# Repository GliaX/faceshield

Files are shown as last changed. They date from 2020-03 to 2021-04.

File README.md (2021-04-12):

# Face Shield
The goal of this project is to create a low cost, high quality, reusable face
shield that can be quickly deployed.

This face shield is currently in use in London, Canada, the West Bank and Gaza Strip.

This face shield's 3D printed design was made by Jake Bender. Contributors include Mike Doell (@mike_doell)
and Mosaic Manufacturing. The injection-molded design was made by Abd Aliwa and Steve Plimmer and can be found at [this branch of the repository](https://github.com/GliaX/faceshield/tree/injection-mold).

To purchase, go to https://store.glia.org

# Bill of Materials
## Molded parts
* 1 head piece (headpiece.stl)

## Other hardware
* 60cm x 1cm Elastic strap
* Large: 28cm x 25cm with a thickness of 0.254mm clear plastic sheet such as Mylar (facesheet-large.svg)
* Small (default): 28cm x 23cm with a thickness of 0.254mm clear plastic sheet such as Mylar (facesheet-small.svg)

# Print instructions
* Use PETG or ABS
* Layer height: 0.3mm
* Use PrusaSlicer 2.2 or above to import 3MF file
* Modify filament and printer settings as needed
* **DO NOT MODIFY PRINT SETTINGS**
* Export and print

# Mylar sheet Instructions
* Cut the mylar sheet with a laser cutter or die cutting machine if available
* If a cutter is not available, you may manually cut the sheets to
28cm x 25cm. Consider rounding corners as per template

# Decontamination
* Disassemble head piece from strap and mylar sheet
* Soak entire shield and strap for 1 minute in warm bleach solution in well-ventilated area
* Rinse with water
* Hang to dry

# Assembly instructions
* See [Assembly Instructions illustration](instructions.jpg) for a visual guide
* Loop strap through strap holes on printed head piece
* Insert clear plastic sheet into printed head piece
* Fit can be adjusted by pulling on the loose ends of the elastic strap

# Licensing notes
As per our understanding, hardware is not covered by copyright. However, we
present our work under the TAPR OHL or GPLv3 licenses insofar as it applies.

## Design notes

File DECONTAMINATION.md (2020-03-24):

# Decontamination
* Make 5,000ppm bleach solution: 85mL of 6.25% hypochlorite household bleach in 1L warm water.
* Disassemble head piece from strap and mylar sheet
* Soak entire shield and strap for 1 minute in warm bleach solution in well-ventilated area
* Rinse with water
* Hang to dry

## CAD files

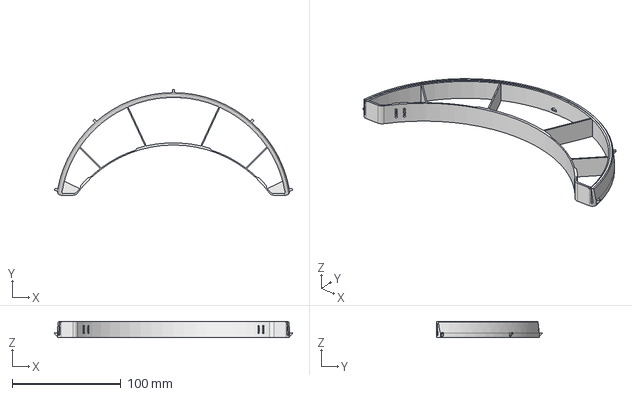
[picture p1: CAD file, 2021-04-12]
source/cad/headpiece.FCStd
218.4 x 96.8 x 15.0 mm

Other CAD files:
source/stl/headpiece.stl

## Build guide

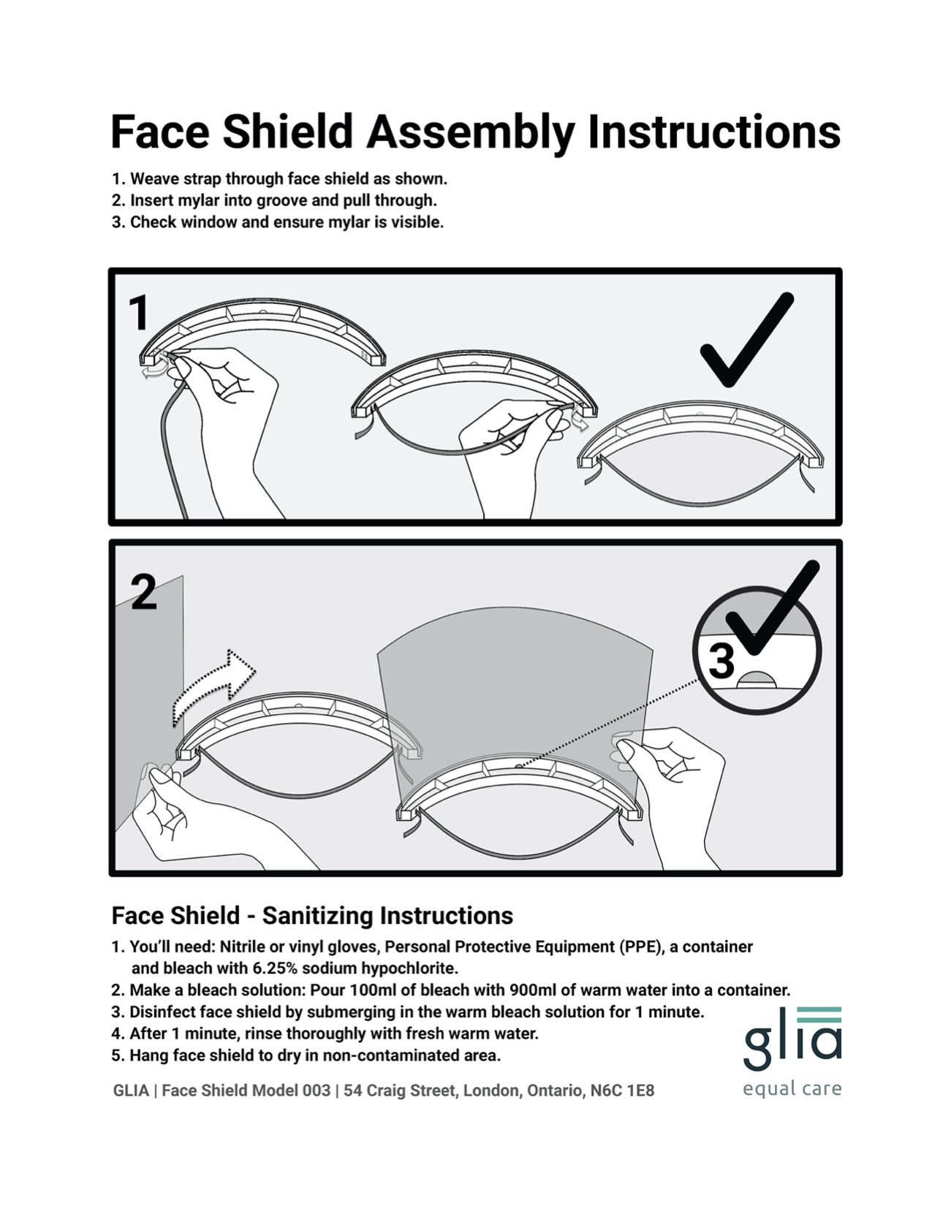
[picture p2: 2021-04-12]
instructions.jpg

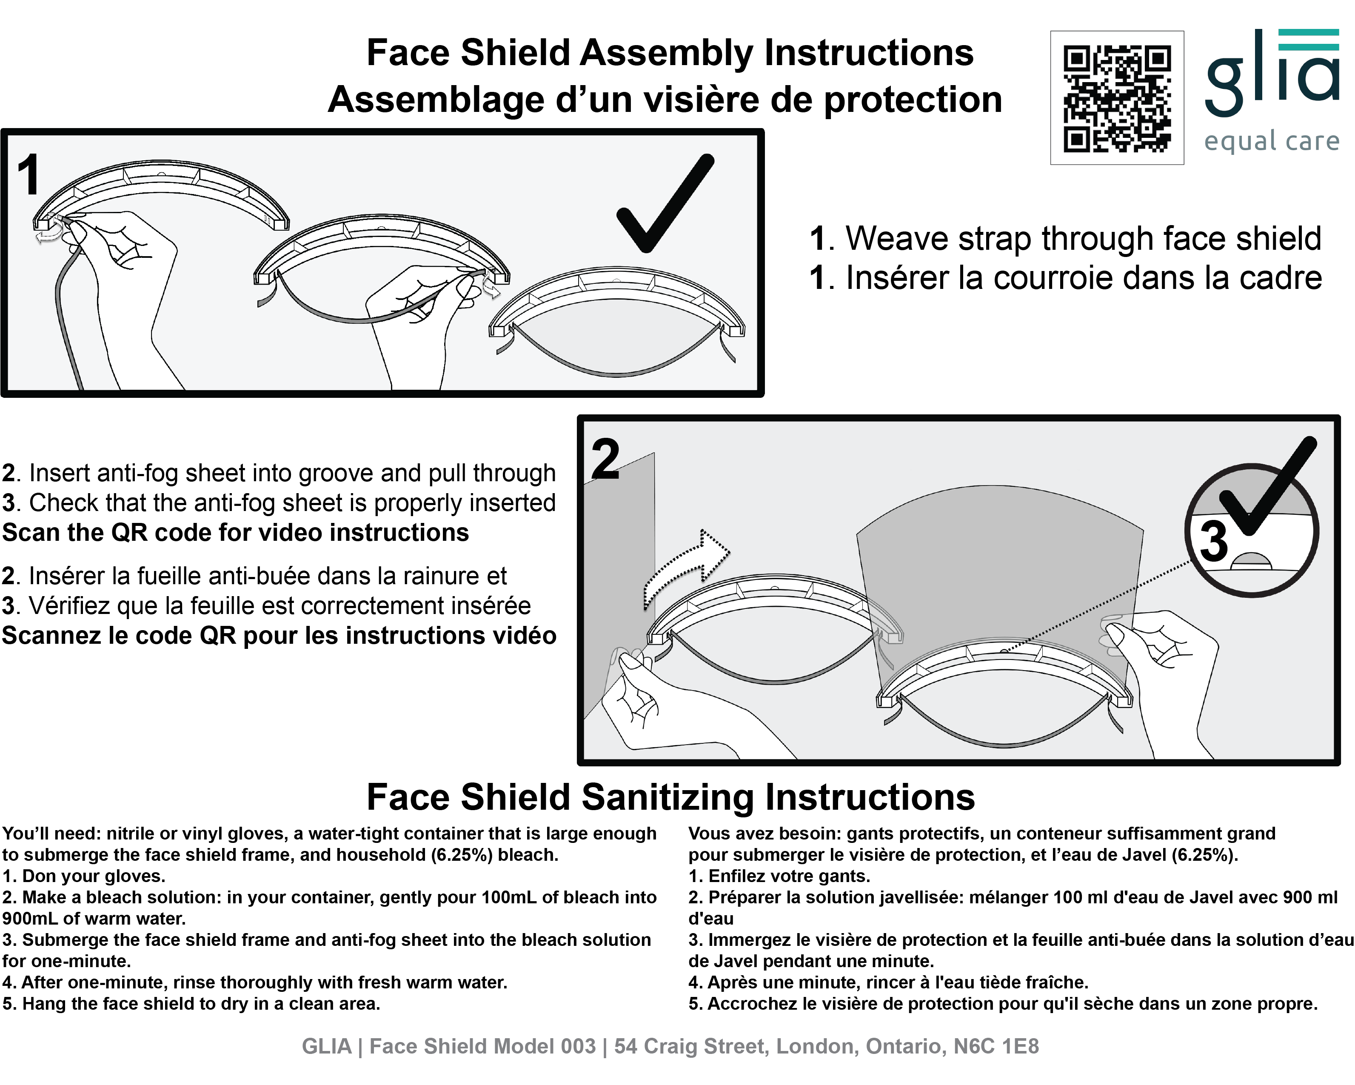
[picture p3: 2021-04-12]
instructions_bilingual.png

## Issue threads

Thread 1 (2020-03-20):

### ISSUE TITLE
Tagging a similar project

### ISSUE THREAD

**Issue by amchagas** [GliaX/faceshield#1]
Hi!
Sorry for the unwanted message here, but I thought it would be worth sharing the efforts being made from the folks at Prusa Research, as they are doing something similar and thinking about doing other tools for health workers (I'm guessing this is something you are already aware of, but in case not): 
https://blog.prusaprinters.org/from-design-to-mass-3d-printing-of-medical-shields-in-three-days/

**Comment by tareko** [comment]
Thank you for this. Unfortunately their project is currently not Free/Libre. A hospital cannot print their masks and use it, as almost any interpretation of CC-By-SA-NC excludes a hospital. I left a message on their prusaprinters page and happy if you have a better way to get in touch with them.

**Comment by kliment** [comment]
I have a direct contact there, @tareko please email me directly and I'll get you in touch. I strongly suspect they are willing to change the license to resolve that kind of issue.

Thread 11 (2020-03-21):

### ISSUE TITLE
is velcro acceptable instead of the printed buckle?

### ISSUE THREAD

**Issue by murtaugh** [GliaX/faceshield#11]

**Comment by tareko** [comment]
Yes, but it just adds a lot more processing. how do you attach the velcro? to where? I wouldn't support adding velcro to the strap as part of our reference design.

I'm closing this, but if I'm missing something and you have a proposal, please don't hesitate

tarek : )

**Comment by murtaugh** [comment]
I was just wondering. I will try it out and see how feasible it is. If it seems workable I'll bring it up again.

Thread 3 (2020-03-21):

### ISSUE TITLE
Missing sheet.svg and mylar thickness

### ISSUE THREAD

**Issue by AnimeEd** [GliaX/faceshield#3]
Hi, I can't seem to find sheet.svg

Regarding the 5mil requirement, how critical is the thickness? Can 4mil and 6mil be used?

**Comment by tareko** [comment]
I haven't made sheet.svg yet. basically rounded rectangle.

As for plastic thickness, it's provider choice. We pick 0.125mm. Thicker is fine, but more expensive. I would suggest not going thinner.

**Comment by tareko** [comment]
Both of these are done in commit 725020ea147522c550765da6c42c1cf00f59d2e9 and c2495cfe5939bce9fe0edbc2ac0be2dfe354fd98

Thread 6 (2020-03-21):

### ISSUE TITLE
New Branch Request - Single Use Disposable Version

### ISSUE THREAD

**Issue by AnimeEd** [GliaX/faceshield#6]
Most health workers are used to single use shields. I'm in contact with a doctor at the local hospital here are some quotes from our discussion

"It's just inconvenient for us to soak
At most they can wipe with a wipe otherwise prob will throw (though later when we are super out of gear it might be different)"

"Vivian Lee: Just putting one patient on a breathing machine you burn through at least 4
For every resp patient you burn through 2 at least"

There is a need for a disposable version (less robust) which is faster to print. One that a single printer can print at least 20 a day.

**Comment by tareko** [comment]
Glia considers disposable face shields wasteful, reckless and a large contributor to our current problem. No institution should use or manufacture disposable face shields.

The current problem is not a lack of PPE, but an excess of disposable PPE that is both destroying our planet and putting healthcare providers at risk due to shortages. Glia is working to end that problem.

After reviewing guidelines, we've reduced soak time to 1 minute. I think that should be fine, and it's hard to believe any institution can't make this happen.

tarek : )

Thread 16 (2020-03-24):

### ISSUE TITLE
Screen Size

### ISSUE THREAD

**Issue by amashari** [GliaX/faceshield#16]
@tareko I had a look at the sizing as you mentioned. I agree triming the height by 2cm makes sense (so from 250 to 230 mm). Width is fine at 280 mm. Would you like me to modify the repo?

**Comment by tareko** [comment]
Thank you Azad. I already did this in this commit: 333020f504ff3777e8f79f0b7b77bea991d7264d . Does that answer the need?

**Comment by amashari** [comment]
yes

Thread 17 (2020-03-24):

### ISSUE TITLE
petg vs pla 

### ISSUE THREAD

**Issue by jeffbrazeau** [GliaX/faceshield#17]
i dont have petg i have lots of pla and resin for my sla printer will they work and then who do i send them to ?

**Comment by tareko** [comment]
Hi!

We haven't tested SLA at all for this. I thought that only some resins were appropriate for medical / FDA use?

Do you mind helping educate me.

tarek : )

**Comment by jeffbrazeau** [comment]
The resin I have is water washable I don’t know how it will react to skin for prolonged contact 

But I have lots of pla for my ender printer 

Will pla work

**Comment by jeffbrazeau** [comment]
Here is the SDS  I don’t know about these things and I am hoping there is someone better then me who knows 

https://cdn.shopify.com/s/files/1/0376/9913/files/PolyJuice-MSDS-NonCasting.pdf

**Comment by lcmyip** [comment]
While I cannot speak for Dr. Loubani, PLA is generally considered a prototyping material, as it is rather brittle and less impact resistant than PETG or ABS. However, if your printer can handle PLA, it can likely also print PETG with minor changes in settings.

I'm not sure that SLA printing would be a cost effective solution for this, especially once you add in the additional post-processing required.

**Comment by amashari** [comment]
PLA is not currently acceptable because of some reports that it is more porous than PETG and ABS and may be more likely to trap virus particles. This is controversial since porocity of prints has numerous factors aside (filament manufacturing process, print settings etc) other than the polymer composition, however it is the current state of the art so we are avoiding PLA.
SLA we have not looked into due to cost and more limited availability of machines. Also most resins are not alcohol resistant. Our cleaning process currently involved household bleach solution so the material would have to be tested with that as well.

**Comment by jeffbrazeau** [comment]
are we not at the point where anything will help pla can be single use

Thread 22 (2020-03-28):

### ISSUE TITLE
Material : PLA

### ISSUE THREAD

**Issue by gcormier** [GliaX/faceshield#22]
I realize PETG/ABS is recommened, but not everyone can print this, or has stockpiles of filament of a specific type.

https://www.billingsclinic.com/foundation/
https://www.billingsclinic.com/app/files/public/4141/3D-Mask-Directions.pdf

This organization is suggesting PLA. Limiting to PETG/ABS limits the number of possible people who can print them.

**Comment by Compunerd-SSC** [comment]
I printed one with PLA to show the concept to my management and I was too lazy to change the filament.  I can tell you that PLA is not a suitable material as it is much too brittle and will crack in the assembly process.  There may also be other reasons to use specific plastics due to cleaning and sanitization requirements or others considerations.

**Comment by volpex-industries** [comment]
In our experience, heat-treating printed PLA will make it stronger and less brittle.  Are there any other reasons not to use PLA?

**Comment by TokenR** [comment]
From my experience:
PLA is hydrophillic. It absorbs water. It also has a low glass transition temperature. Keep it in the car on a hot sunny day and it will melt and deform. Over time, PLA will crack and deform. Layer adhesion is fair, but not exceptional like PETG or Nylon. It is a more rigid plastic - and while it is good in terms of hardness, it isn't as tough as PETG.

PETG is hydrophobic. It does not absorb water. It has a higher glass transition temperature and it has good layer adhesion. It won't delaminate unless the layers are printed at the wrong temperature. This makes it a better material because it can be reused after gas autoclave decontamination. PETG is food safe and doesn't leech like PLA.

The print uses a "clip" mechanism to hold the shield in place with friction. PLA isn't tough enough to flex and will crack and snap if overstressed.

If your printer hot end can manage 255-260 degrees C and your bed can manage 90 degrees C, PETG should be within reach of your printing capabilities. A lower nozzle temperature risks delamination depending on the brand of PETG you may be using.

**Comment by volpex-industries** [comment]
Heat-treating PLA deals with most of those factors; it ends up stronger and stiffer, and from what I understand is also less porous, which might help against water absorption.  It can make the part shrink a bit, but we can adjust the print for that with some experimentation.  And since this is emergency production for COVID-19, and we'll be producing them for cost of materials, long-term life isn't such an issue as long as they can last long enough to help cover for the PPE shortfall until the proper industrial supply chains get their acts together and produce enough to fill the need.

We'll test our first few as much as we can, of course.  We can go to PETG if we need to, just need some parts (probably just a better bed heater) which will mean delays before we can start production, and it'll mean we need to order a bunch of PETG instead of using all the PLA we already have.

**Comment by TokenR** [comment]
Annealing reflows the plastic's mechanical structure, but the chemical properties of the plastic itself don't change.

This is a high stress situation where mixing materials is not safe. I understand it's an emergency situation - which is why I intend to only print in PETG as it won't fail. One failure at the wrong time would be very very bad, and the lives of those that are being protected by these devices are critical to not only this pandemic, but to the next one.

I would ask that anyone who is printing these to please mark your devices with the material it is manufactured from and with the company/person who manufactured them. If one of us manufactures a large lot of defective items, they must be readily identified and the issues must be isolated. Conversely, if specific items are found to be of better quality, that information can be disseminated to others to bring their manufacturing standard up.

**Comment by tareko** [comment]
Thank you all for your comments. In addition to several infection-control issues (hydrophillic, porous), the mechanical issues are not acceptable. In Gaza, temperatures are routinely high enough to deform PLA parts in routine storage (no electricity, thus no AC). We use ABS there and PETG in Canada as a result.

At the end of the day, we have to make some editorial decisions. This is one of them. I'll close the issue for now, but don't hesitate to continue the discussion as desired.

tarek : )

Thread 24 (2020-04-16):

### ISSUE TITLE
Bulk stl

### ISSUE THREAD

**Issue by kfrancis** [GliaX/faceshield#24]
My printer can handle much much more of these at a single time, but I'm not sure how to stack these in a good way. Is that something possible? I'm using the [AnyCubic Predator](https://www.anycubic.com/collections/predator-series/products/anycubic-predator-fdm-printer) which has a print volume of 370×370×455mm.

**Comment by mza1979m** [comment]
I would just stack them in whatever way is most optimized, so that you can fit as many on the plate as you possibly can. For example, one of my printers is an AnyCubic Chiron (400x400x450), and I managed to fit 9 on the plate (see screenshot).
![anycubic_chiron](https://user-images.githubusercontent.com/16178388/77808663-a83e9100-7062-11ea-8ae7-be5dad1b9b2f.jpg)

**Comment by kfrancis** [comment]
Yea, ok. That's fine.

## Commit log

2020-03-20 Add source files and printables
    [buckle.stl, faceshieldx1.3mf, faceshieldx2.3mf, headpiece.stl]
2020-03-20 suggest the mylar sheets can be cut with a die cutter
2020-03-21 Added width to elastic strap and formatting nit.
2020-03-21 add a reference to an acceptable mil value for the mylar
    mylar is often sold using mils to denote thickness; 5mil is .127mm
2020-03-22 Version 2.0 release
    [faceshieldx1.3mf, faceshieldx2.3mf, headpiece.stl]
2020-03-22 Reduce Elastic strap length
2020-03-23 Add retraction to prevent oozing after printing is done
    [faceshieldx1.3mf, faceshieldx2.3mf]
2020-03-23 Source CAD files from Mike Doell
    [buckle.stl, headpiece.igs, headpiece.step, headpiece.stl]
2020-03-26 Upgrade to version 2.1
    [faceshieldx1.3mf, faceshieldx2.3mf, headpiece.stl]
2020-04-05 Remove skirt
    [faceshieldx2.3mf]
2020-06-05 Upgrade to v3 shield design
    [buckle.stl, faceshieldx1.3mf, faceshieldx2.3mf, faceshieldx3.3mf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]
2020-07-31 Headpiece v3.1
    Updated headpiece:
    * better accommodates the elastic strap that Glia is currently using
    * improves strength between the two strap holes on either side
    Next steps:
    * integrate Glia logo into headpiece
    [headpiece.stl]
2020-09-22 headpiece v3.2
    * improved strap hole strength
    * added covered top option (it is a hidden extrusion)
    * improved print quality
    [facepiece.stl, faceshieldx1.3mf, faceshieldx3.3mf, headpiece.FCStd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]
2020-09-22 fixed error
    facepiece —> headpiece
    [headpiece.stl]
